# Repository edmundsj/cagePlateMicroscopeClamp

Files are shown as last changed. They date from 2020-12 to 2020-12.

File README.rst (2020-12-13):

Thorlabs 30mm cage plate holder (CP33)
========================================

In order to attach an optical cage system to a microscope, I created this.

Features
---------
- Fits one 30mm cage sytem thorlabs cage plate
- Has flaps with two holes on either side to screw into a substrate

Getting Started
--------------------

To generate an STL file for this project, you need to do the following (if you want to modify the STL, otherwise just download it).

Installing Dependencies
~~~~~~~~~~~~~~~~~~~~~~~~

If you have not already, install the [openSCAD](http://www.openscad.org/) and [openpyscad](https://pypi.org/project/openpyscad/)

Issues 
------------------------
1. [FIXED v2] Holes came out too small for screws. I specified 2.6, but the holes came out at ~2.0mm, and the screws appear to be closer to 3mm in diameter. 
2. [FIXED v2] Holes are too close to wall and I cannot screw the things in, becuase the screw caps are butting against the wall. Screw head diameter is 6mm, so I need 1.5mm of clearance from the hole on either side.
3. [FIXED v2] The rods are partially covered on either side, the groove for the cage plate is too deep. It measures ~4mm, it needs to measure no more than 2mm.
4. The whole thing needs to be slightly less wide - it doesn't fit within the tabs on the microscope screw holder. At least 4mm needs to be cut off from the tabs on the side.
5. If the whole thing were just a smidge taller 

Notes
--------
- The screw pitch is almost perfect, and I think should do just fine.

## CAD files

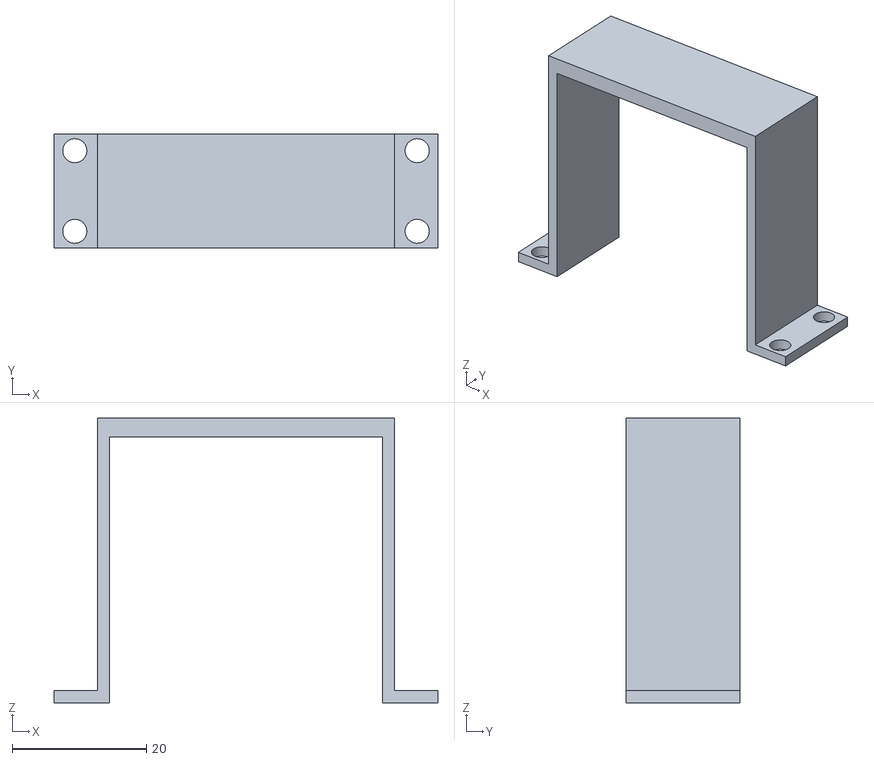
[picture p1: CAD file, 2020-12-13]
thorlabs_cage_adapter.stl
57.2 x 17.0 x 42.4

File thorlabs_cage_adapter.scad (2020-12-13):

$fa=0.5;
$fs=0.5;
difference(){
    cube(size=[57.2, 17, 42.4]);
    translate(v=[-0.01, -0.005, 1.8]){
        cube(size=[6.51, 17.01, 40.61]);
    };
    translate(v=[50.71, -0.005, 1.8]){
        cube(size=[6.51, 17.01, 40.61]);
    };
    translate(v=[8.3, -0.005, -0.01]){
        cube(size=[40.6, 17.01, 39.61]);
    };
    translate(v=[8.3, 4.05, 0]){
        cube(size=[40.6, 8.9, 40.6]);
    };
    translate(v=[3.1000000000000014, 2.5, -0.005]){
        cylinder(h=1.81, d=3.6);
    };
    translate(v=[54.1, 2.5, -0.005]){
        cylinder(h=1.81, d=3.6);
    };
    translate(v=[3.1000000000000014, 14.5, -0.005]){
        cylinder(h=1.81, d=3.6);
    };
    translate(v=[54.1, 14.5, -0.005]){
        cylinder(h=1.81, d=3.6);
    };
};

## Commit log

2020-10-22 wrote code for version 1, submitted
    [thorlabs_cage_adapter.scad, thorlabs_cage_adapter.stl]
2020-12-13 updated README, code, for latest version of design
    [thorlabs_cage_adapter.scad, thorlabs_cage_adapter.stl]
